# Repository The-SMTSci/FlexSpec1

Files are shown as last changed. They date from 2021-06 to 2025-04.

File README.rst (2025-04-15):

FlexSpec1
=========

 

Small telescope Flexible Spectrograph One.

Check out the documentation: 

`FlexSpec1 ReadTheDocs.io <https://flexspec1.readthedocs.io/en/latest/>`_

Serial Ports
------------

The later Rpi 4's are based on BCM2835 processor, and uses the
PL011 UARTs. 

.. list-table:: RPi 4 UART and Device Assignments
   :widths: 10 25 25 50 50
   :header-rows: 1

   * - UART
     - RX Pin (Board)
     - Tx Pin (Board)
     - Comm Port
     - Conflicts
   * - uart0 
     - GPIO 14    8  
     - GPIO 15   10  
     - /dev/ttyAMA0 
     - Serial Console
   * - uart1 
     - GPIO 0    27  
     - GPIO 1    28  
     - /dev/ttyAMA1 
     -
   * - uart2 
     - GPIO 4     7  
     - GPIO 5    29  
     - /dev/ttyAMA2 
     - I2C
   * - uart3 
     - GPIO 8    24  
     - GPIO 9    21  
     - /dev/ttyAMA3 
     -
   * - uart4 
     - GPIO 12   32  
     - GPIO 13   33  
     - /dev/ttyAMA4 
     - SPI0
   * - uart5
     - GPIO 12   14
     - GPIO 13   15
     - /dev/ttyAMA5

Other Interfaces
----------------

# Enabling I2C3, with SDA on GPIO4 and SCL on GPIO5
dtoverlay=i2c3,pins_4_5

History:
--------

V0.0 - pre-release placeholder.





PuTTY Commands:
+++++++++++++++

.. list-table:: PuYTTY FlexSpec1 Serial Port Commands
   :widths: 10 25 90
   :header-rows: 0

   * - A<CR>
     - 
     - All functions list
   * - B<CR>
     - 
     - Blue LED
   * - C<CR>
     - 
     - Configuration to set the grating lines per mm
   * - F<CR>
     - 
     - Focus the collimating lens
   * - G<CR>
     - 
     - Green LED lights the Green
   * - H<CR>
     - 
     - Home The Grating
   * - I<CR>
     - <PWM>
     - Incandescent Grain of Wheat Flat lamps, PWM 0 - 100%.
   * - J<CR>
     - 
     - Used to center zero order to focus on slit
   * - L<CR>
     - <PWM>
     - Flat Lamp lights the LED Flat lamps, PWM 0 - 100%.
   * - M<CR>
     - 
     - Reset collimating Focuses to zero
   * - N<CR>
     - 
     - Neon / Calibration
   * - O<CR>
     - 
     - Off Turns all lamps off
   * - Q<CR>
     - 
     - Query status of the spectrometer
   * - R<CR>
     - <PWM>
     - Red LED Controls The Red LED With PWM 0 - 100%
   * - S<CR>
     - 
     - Shutter  (Open Close Toggle)
   * - U<CR>
     - <PWM>
     - UV Boost Lights the UV Boost, PWM 0 - 100%.
   * - V<CR>
     - 
     - Viewer for Slit. Backlight View the slit with backlight
   * - W<CR>
     - <Integer>
     - Wavelength rotate the grating to center desired wavelength
   * - Z<CR>
     - 
     - Zero Collimating lens to position = 0 (home)
   * - 
     - 
     - (This should only be done once on initialization of
   * - 
     - 
     - physical focus)
   * - 
     - 
     - 
   * - ?<CR>
     - 
     - Query the Defines the grating and collimating motor direction
   * - 
     - 
     - (This should only be done once on initialization or
   * - 
     - 
     - if a motor is changed depending on the manufacture
   * - 
     - 
     - some motors run in oposit direction)

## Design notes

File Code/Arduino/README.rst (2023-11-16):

FlexSpec1 Arduino Directory
===========================

An Arduino program consists of a *.ino* file, that acts like the main program.

The Arduino IDE/Compilers require the .ino file to be in a directory with the
same name. For example:  demos/hello/hello.ini is inside a directory called hello.

Any other file in the directory that ends in *.c*, *.cpp*, *.h*" will also
be compiled and linked into the code. So if you have a file call extras.cpp
and you want to keep it around as a temporary backup call it extras.cpp.bak
and it will be ignored.

Arduino code ***IS*** "--std=c++11" and "-fno-exceptions". This means quite
a few interesting new code features are available, like auto, looping extensions
etc. However it also means that "try/throw/catch" exception mechanism is 
disabled. The exception mechanism uses quite a bit of code.

Avoid anything that refers to "iostream" This brings in quite a lot of code.

C is a proper subset of C++, so do not feel compelled to use lots of C++
features.

ARM Boards, BLE/IoT and Seeduino Xaio
-------------------------------------

Boards are made to be compilent with different vendors environments. One is Mbed
and the other is SAMD. In some cases, libraries are written to take advantage
of only one environment's features! Thus code that compiles on one will fail
on another.

In the main .ino file, please use the IDE to gather the version and author's
name for each library package used. This helps to avoid confusion later.

This Directory
--------------

1. Demos
   a. hello : Print the word hello to the serial ports.
   b. gigo: Characters that are read, are printed right back. Handy for testing the CR/LF and baud rates.
2. MainBoard
   a. FlexSpec
3. Kzin
   a. Kzin

Serial Communications
---------------------

The USB hardware in Arduinos, may not work well with the USB hardeare
found in hubs and main motherboards. This does cause some issues.

The clock rates of Arduinos are not that precise. 9600 baud may be 
a tad bit slower/faster -- but the protocol usually does not trip
over small differences.

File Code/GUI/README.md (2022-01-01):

GUI
===

The GUI has several subsystems:

# The "matching classes" py together with Arduino's C++
# The underlying algorithms as resources, now being developed under
# django in a container.

FlexSpec1/Code/GUI/

README.md
main

---
2021-12-31T11:36:29-0700

Zoom meeting: 3 papes:
1) collimator (maths etc)
2) guider (maths etc)
3) kzin ring (flats)
Perhaps a few newsletters...

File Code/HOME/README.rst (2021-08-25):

README
======

The HOME directory has some basic things to copy to home directories
for users of the Raspberry Pi.

pi.aliases - aliases, and alterations to terminals to make the system
  livable.

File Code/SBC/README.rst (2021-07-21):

Single Board Computer Code
==========================

This directory holds the code needed to support the Bokeh interface
to the rest of the world.

server.py -- The stub of a server. DEVELOPING

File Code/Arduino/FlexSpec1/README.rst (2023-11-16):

FlexSpec1
=========

The current version is 4.1.2, its md5sum is: db0fdba5357043d4d449a2c6e9d09390.

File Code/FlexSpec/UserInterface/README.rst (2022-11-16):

README
======

Testing can be done with Chrome in incognito mode (does't clutter
up cookies).

This approach uses a "matched class" and a "data driven" approach.
The 'def send_state(self) is the gateway to Flex dispatch server for
    each class.

FlexSpec.py - instantiate/layout the gadgets we're currently supporting:
   KzinBokeh.py
   Collimator.py
   GratingBokey.py GrratingDefinition.py
   ParallacticAngle.py
   Shutter.py  (Needs to be developed fully)

Other Gadgets:
      EEPROMBokeh.py
      BlinkyBokeh.h

Good to have:
     Site.py
     TargetsBokeh.py
     FITS/FITS.py       -- brew up header for the instrument

The objects to use/develop:

    BlinkyBokeh.py       - Test more than anything
    CameraFocusBokeh.py  - NOT the 'camera' lens
    Collimator.py        - drive the collimator motors
    EEPROMBokeh.py       - manage an eeprom filesystem     FlexEEPROM.py        -
    FITS.py              - FlexSpec FITS header details, fits format
    FlexSpec.py          - A class for the device itself
    GratingBokeh.py      - Motors and configuration of  a grating
    GratingDefinition.py - Definition of lots of gratings to choose
    Guider.py            - NOT focus/rotate the guider
    KzinBokeh.py         - Manage the cal lamps and the shutter
    LampBokeh.py         - ?
    Network.py           - GUI/Dispatch server management
    ParallacticAngle.py  - pangle - get/report the parallactic angle
    Shutter.py           - Deal with the shutter itself
    Site.py              - Site details
    SlitBokeh.py         - Select and manage slit details
    TargetsBokeh.py      - NOT state the curent target details

TBD: FITS.py, Site,Targets. Network

Not clearly defined.... FlexPublish.py       -

RunFlexSpec

Two classes -- A python class at the Bokeh level and a C++ class in the
Arduino have their data synchronized. The user's request is tested and all
error checking in performed at the Bokeh class then an image of the
variables' state is sent to the matched Arduino C++ partner class.
The C++ class strives to "match the request" and will achieve a final
state. For example a request for 5000 angstroms for a grating's central
wavelength may fall between 4995 and 5007 due to cogging of the control
motor. Assuming perfect backlash, the C++ class may choose 4995. It
then reports its state back to the Bokeh class -- the Bokeh updates
the user's interface to reflect the "current state-of-affairs" of the
remote device. The governing rule is the remote device takes precedence
over the display. The display strives to portray the remote state-of-affairs.

Release Note:
2022-08-09T08:20:31-0600

Several modules were sending actual non-quoted integer/float
values. This was corrected though there may be a few missed
cases. While the code was open, a few major internal changes
were implemented. This does not effect the general operation.

The main visible change is the 'Display' pane now outputs
text that may be cut then pasted into Python. This is more
for checking results by hand. This work is leading to
a log message.

The code was re-worked for formatting, nomenclature (Display was
changed to FlexPublish to reflect what it really does), the layout
variable names changed to reflect their actual order etc.  Comments
were added, formatting of the code, usual beautification things.

Work has began on the serial interface extension(s) to the
main backend dispatch server. Written in python, with the
target machine being the Raspberry Pi 4B+.

.. note::

    myapp
       |
       +---__init__.py
       +---app_hooks.py
       +---main.py
       +---request_handler.py
       +---static
       +---theme.yaml
       +---templates
            +---index.html

.. note::

    myapp
       |
       +---__init__.py
       |
       +---app_hooks.py
       +---data
       |    +---things.csv
       |
       +---helpers.py
       +---main.py
       |---models
       |    +---custom.js
       |
       +---request_handler.py
       +---static
       |    +---css
       |    |    +---special.css
       |    |
       |    +---images
       |    |    +---foo.png
       |    |    +---bar.png
       |    |
       |    +---js
       |        +---special.js
       |
       |---templates
       |    +---index.html
       |
       +---theme.yaml

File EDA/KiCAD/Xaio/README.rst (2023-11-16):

Xaio Standalone Board
=====================

Schematics
-----------

KiCAD Files
-----------

* XAIO-B1-A-cache.lib
* XAIO-B1-A-rescue.dcm
* XAIO-B1-A-rescue.lib
* Xiao-B1-cache.lib
* Xiao-B1.kicad_pcb
* Xiao-B1.pro
* Xiao-B1.sch
* Xiao-KM1-a-cache.lib
* Xiao-KM1-a-recover.pro
* Xiao-KM1-a.d356
* Xiao-KM1-a.kicad_pcb
* Xiao-KM1-a.pro
* sym-lib-table

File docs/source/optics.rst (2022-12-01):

Care of Optics
==============

When handling optics uses gloves, nitrile or pure clean untreated
cotton gloves. This will protect the optical elements and protect
you from harsh cleaning chemicals. Optics should be stored in an
airtight container to avoid reaction with pollutants. 

#.  **Never** use silcone based adhesives or silicone based lubricants any 
    where near optics. They outgas and condense on the optical surfaces.

#.  The optics should never be touched with your bare hands.  Always
    use clean powder free latex or nitrile gloves. Finger prints leave
    oils, acids and other volatiles on the surfaces which in the cases of
    gratings can not be removed. On lenses or mirrors they may etch the
    surface coatings.

#.  If after careful handling a finger print gets on the surface a
    micro fiber cloth may remove it if used gently.  DON’T try to wipe a
    grating it will scratch.

#.  Front surface mirrors are also fragile. Usually they are over
    coated for protection but the coating may be very thin.

#.  Don’t use **Windex** |reg| to clean optics. It contains ammonia which
    can remove aluminum coating. Use Everclear |reg| grain alcohol, 95%
    ethanol alcohol or commercial lens cleaning solution as a cleaning
    fluid. Us it sparingly. Grain alcohol does not contain denaturing
    agents and should not leave a fine white powder on optics.

    Like most alcohols, isopropyl alcohol reacts with active metals
    such as potassium to form alkoxides that can be called
    isopropoxides. The reaction with aluminum (initiated by a trace
    of mercury) is used to prepare the catalyst aluminum
    isopropoxides. Most IPA isopropyl alcohol has denaturing
    agents added and will leave a fine white powder.

#.  Gratings are very susceptible to handling problems. Even with
    gloves never touch the ruled surface.  Any scratches or finger prints
    will introduce scattered light in to the system. A spectrograph is
    always starved for light and to scatter some of the light will reduce
    the throughput.

Tips for optics in a spectrograph
---------------------------------

#.  Grating orientation: if a commercial blazed grating is used it
    will have an arrow drawn on the top, bottom or both edges that are
    perpendicular to the grooves.  This arrow shows the blaze
    direction. The arrow should point toward the incoming beam.  This
    orientation maximizes the energy into the first order. If the
    arrow is missing it is possible to look into the spectrographs
    camera port, without the camera lens in place, while light is
    shinning on the slit, rotate the grating so that the zero’th order
    can be seen. Then rotate the grating further to pick up the
    spectrum starting with the blue end. Further grating rotation will
    the bring up the second order. The first order should be very much
    brighter than the second order.  If it isn’t the grating
    orientation in the holder should be reversed.

#.  If the dispersion along the image from the sensor is not
    horizontal (follows a 'row' of pixels), the camera needs to be
    rotated such that it is. 

#.  If the calibration lamp emission lines are not vertical with
    respect to the grating; the OVIO slit needs to be rotated in it’s
    holder to make them vertical. This can be fiddly sometimes to get
    right. Also the vertical slit must be co-linear with the grating
    grooves.

#.  If lenses are not a snug fit into their holders a small
    application of white glue on the holder will hold them in place
    but allow later removal if needed. Don’t get a glue string on the
    lens.

#.  If the lens is a snug fit into the holder make sure that you don’t
    apply too much pressure to insert it. Some lower quality achromat
    lens elements are not glued in a way that is precisely centered
    and while pushing it in an edge might get caught and split the
    elements apart.

#.  Depending on many factors (lens focal length, aperture, quality)
    the blue and red ends of the spectra may be out of focus while the
    center is sharp. This is normal with simple achromat lenses used
    for the camera lens. If a commercial photographic lens is used for
    the camera lens this is much less of a problem as the multiple
    elements in the commercial lens are designed to flatten the field.

#.  When combined with large chips, short focal length lenses, with
    short radii may require the sensors plane to be shifted. This is
    easily achieved with after-marked sensor/camera tilt correctors.

#.  A Cheshire eyepiece (laser collimator) is a very handy tool to get
    things lined up in the spectrograph, particularly the guide mirror
    and main mirror. It is also an easy way to check if the grating is
    mounted with it’s surface parallel with the rotation stage. If it
    is a green laser and the grating stage rotated till the beam is
    centered in the camera port, then the first spectra will be close
    to centered. If red then adjust the grating angle such that it is
    where H-alpha emission is expected on the image.

#.  Achromat lens orientation. When mounting lenses the side with the
    bigger “bulge” should be oriented toward the grating. Both for the
    collimating lens as well as the camera lens.

.. |reg|    unicode:: U+000AE .. REGISTERED SIGN
.. |copy|   unicode:: U+000A9 .. COPYRIGHT SIGN

Adhesives
---------

ASTM E595 is the specification for low outgassing. 

Outgassing Data for Selecting Spacecraft Materials Online

https://outgassing.nasa.gov/

PDF about gasses of common filiments:
https://www.mdpi.com/1420-3049/27/12/3814/pdf?version=1655194705

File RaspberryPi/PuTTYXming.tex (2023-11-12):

% PuTTYXming.tex

\section*{PuTTY and Xming on Windows} \label{sec:puttyxming}
\setcounter{section}{1}

PuTTY running remotely on a Raspberry Pi uses X11 to share its
interface with the remote user. This may require XMing for Win11, and
XQuartz for Apple machines. It may require including a X11 desktop (in
lieu of Wayland) on the remote Linux machines.

This article addresses executing PuTTY on a Raspberry Pi from a Win1X
machine located elsewhere on the Internet. It addresses basic tactical
aspects of network configuration. Direct X11 and port-to-port TCP
methods sidestep the bandwidth overhead of VNC like environments.  The
office desktop is presumed to be a Win1X office desktop, but may be a
Linux desktop with built-in native X11 protocols\footnote{In X11, the
  XClient is the program with all the builtin domain/control logic --
  like a spreadsheet, that offers up a GUI connection. An XServer,
  with all the logic for window creation, managing user interaction
  and 'serving' back graphics etc ties the user to the XClient's
  logic. The XServer may be elsewhere on the network from the running
  program. The protocol is very light-weight compared to
  remote-desktop (VNC) methods.}\footnote{Note: The Wayland
  X11-Replacement may introduce X11 issues.}, or an Apple machine with
a proper X11 Server support package like XQuartz.  Linux is addressed
in section \ref{sec:PuttyLinuxDesktop}.

Win1X requires an X11 Server support program. Here the
Xming\footnote{Get Xming: https://sourceforge.net/projects/xming/} package is the
only one discussed.

The typographic conventions used in these notes.

Here \llbox{k} means hit the ``k'' on the keyboard. 

For the Win1X office desktop, it is important that you acquire and install:
\vspace{-.15cm}
\begin{enumerate}\addtolength{\itemsep}{-0.5\baselineskip}
%\setcounter{enumi}{N}
   \item   Win1X office desktop
\vspace{-.15cm}
\begin{enumerate}\addtolength{\itemsep}{-0.5\baselineskip}
%\setcounter{enumi}{N}
   \item   XMing
   \item   PuTTY
\end{enumerate}
   \item   Raspberry Pi
\vspace{-.15cm}
\begin{enumerate}\addtolength{\itemsep}{-0.5\baselineskip}
%\setcounter{enumi}{N}
   \item   PuTTY
\end{enumerate}
   \item   Optional Linux office desktop
\vspace{-.15cm}
\begin{enumerate}\addtolength{\itemsep}{-0.5\baselineskip}
%\setcounter{enumi}{N}
   \item   PuTTY
\end{enumerate}
\end{enumerate}

You need to configure XMing's XLaunch program. You need to configure the
Raspberry Pi's configuration.

The PuTTY program provides a X11/ssh connection to remote machines. Here
the machine's hostname is \dhl{stellarmate.local}, the port is 22.

Xming is a X11 ``server'' (meaning is backwards from a data center's
client/server sense). X11 ``serves'' the graphics from a remote machine
doing all the heavy computing on a light-weight machine that knows nothing
about the remote application.

Grab Xming and install on a Win machine.

First some X11 magic:

You will open a \dhl{ssh -X} connection to the Raspberry Pi. This
allows linux to display a console window on the Win1X office desktop
monitor. In that window (remember will start programs on the Raspberry
Pi) you will start a PuTTY program running on the Raspberry Pi that
causes its window to appear on the Win1X office desktop.

\begin{figure}[h!]
\centering

\caption[Win1X use.]{Win1X office desktop monitor uses TCP/IP and SSH
  with the -X switch to open a connection to Raspberry Pi. A PuTTY
  instance is started on the Raspberry Pi, configured for the USB port
  for the Arduino displays the PuTTY window on the remote desktop vi
  SSH -X working with Xming} %% \caption{{\tiny{citation}}}
\label{figure:Diagram1}
\end{figure}

\begingroup \fontsize{10pt}{10pt}
\selectfont
%%\begin{Verbatim} [commandchars=\\\{\}]
\begin{verbatim} 

Check the files in the /etc/X11 directory:
   /etc/X11/xinit/xserverrc
   ~/.xinitrc
   ~/.xsession  -- start programs when the login is complete
   ~/.profile

ssh-keygen -t ed25519 -C "your_email@example.com"

\end{verbatim}
\endgroup
%% \end{Verbatim}

If there is no /etc/X11

\verb=xmodmap -pke > ~/.Xmodmap # make a .Xmodmap upon which to hack=

This varies with new modern keyboards, there is massive
confusion over what a key is called and what code corresponds to
the key among keyboard vendors. 

To use the \dhl{caps lock} key as a spare \dhl{control} key find the
code for the caps lock key using the \dhl{xev} program. Xev will show
keycodes when a key changes state, like shift down, then shift up
etc...  

Hit the the ``caps'' key and note its code. Then edit the \dhl{~/.Xmodmap}
file and change:

\verb/keycode  37 = Control_L NoSymbol Control_L/

\newpage
\subsection{Remote Desktop PuTTY}

On the remote desktop, configure the remote PuTTY:

\vspace{-.15cm}
\begin{enumerate}\addtolength{\itemsep}{-0.5\baselineskip}
%\setcounter{enumi}{N}
   \item   Session:
\vspace{-.15cm}
\begin{enumerate}\addtolength{\itemsep}{-0.5\baselineskip}
%\setcounter{enumi}{N}
   \item   Select the \dhl{Serial} radio button
   \item   Serial Line to \dhl{/dev/ttyACM0}
   \item   Speed \dhl{9600}
   %\item   CTM\_X
   \item   Close window on exit $\rightarrow$ \dhl{Only on clean exit}
\end{enumerate}
   \item   Terminal
\vspace{-.15cm}
\begin{enumerate}\addtolength{\itemsep}{-0.5\baselineskip}
%\setcounter{enumi}{N}
   \item   In the \dhl{Line disipline options}:
\vspace{-.15cm}
\begin{enumerate}\addtolength{\itemsep}{-0.5\baselineskip}
%\setcounter{enumi}{N}
   \item  Local echo to \dhl{Force on}
   \item  Local line editing to \dhl{Force on}
\end{enumerate}
\end{enumerate}
   \item   Window
\vspace{-.15cm}
\begin{enumerate}\addtolength{\itemsep}{-0.5\baselineskip}
%\setcounter{enumi}{N}
   \item   Columns: \dhl{120} Rows: \dhl{50}
   \item   scrollback 200
   \item   display scrollbar
   %\item   Reset scrollback on display activity
   %\item   push erased text into scrollback
\end{enumerate}
   \item   Connection $\rightarrow$ Data
\vspace{-.15cm}
\begin{enumerate}\addtolength{\itemsep}{-0.5\baselineskip}
%\setcounter{enumi}{N}
   \item   login name can be set to \dhl{stellarmate} for stellarmate, or
     the remote user's name.
   \item   Terminal-type string xterm
   \item   Terminal Speed 38400, 38400
\end{enumerate}
\item SSH
\vspace{-.15cm}
\begin{enumerate}\addtolength{\itemsep}{-0.5\baselineskip}
%\setcounter{enumi}{N}
   \item   Remote Command to \dhl{/home/stellarmate/bin/flex.py}
\end{enumerate}

   \item   SSH$\rightarrow$X11

\vspace{-.15cm}
\begin{enumerate}\addtolength{\itemsep}{-0.5\baselineskip}
%\setcounter{enumi}{N}
   \item   Enable X11 forwarding
   \item   localhost:0.0
   \item   MIT-Magic-Cookie-1
\end{enumerate}
\vspace{-.15cm}
\begin{enumerate}\addtolength{\itemsep}{-0.5\baselineskip}
%\setcounter{enumi}{N}
   \item   Serial
\vspace{-.15cm}
\begin{enumerate}\addtolength{\itemsep}{-0.5\baselineskip}
%\setcounter{enumi}{N}
   \item   Baud to 9600
   \item   Data bits 8
   \item   Stop bits 1
   \item   Parity None
   \item   Flow Control None.
\end{enumerate}
\end{enumerate}

\end{enumerate}

\begin{figure}[h!]
\centering

\caption{PuTTY screen snaps of the 4 configuration menu panels.} %% \caption{{\tiny{citation}}} 
\label{figure:PuYYTXming}
\end{figure}

\newpage
\subsection{Remote Desktop Xming}

On the Windows pane, enter a new configuration for this machine.

\vspace{-.15cm}
\begin{enumerate}\addtolength{\itemsep}{-0.5\baselineskip}
%\setcounter{enumi}{N}
   \item Page 1 - Set Multiple windows (Each remote application gets
     its own Win1X office desktop window).
   \item Page 2 - Start no client. The clients are started with the
     Win1X PuTTY's SSH -X session.
   \item  Page 3 - Clipboard (handy)
   \item Page 4 - Save the configuration. This sets the policy for all
     machines, Xming does not care about the remote machines business
     -- any remote may connect if firewall permissions are set.
\end{enumerate}

\begin{figure}[h!]
\centering

\caption{Xming screen snaps of the 4 configuration menu panels.} %% \caption{{\tiny{citation}}} 
\label{figure:XmingConfig}
\end{figure}

\input{Raspberry.tex
}

\subsection{StellarMate} \label{sec:StellarMate}

You need to \dhl{sudo apt update}, then \dhl{sudo apt install putty -y}
to install PuTTY.

Add the \dhl{x11-utils} package to pick up the rather silly command
xeys. This displays two white eyeballs and the pupils track the mouse
movement. While small and cute, it does a rather deep test of the X11
capability including managing the event manager. This is helpful
to debug X11 connnections.

\begin{quote}
\dhl{sudo apt install -y x11-utils}
\end{quote}

Other programs:
\begin{quote}
\dhl{sudo apt install -y saoimage-ds9}  \\
\dhl{sudo apt install -y iraf}          \\ 
\dhl{sudo apt install -y python3-pyraf}
\end{quote}

The ssh connect to StellarMate is made to an alternate port:

\dhl{ssh -X -p 5624 stellarmate@stellarmate.local}

The username is \dhl{stellarmate} and the password is the usual
StellarMate password.

\section{Using Putty from Linux Desktop} \label{sec:PuttyLinuxDesktop}

PuTTY on a linux desktop machine in the office has all the Xming features
built-in and does not require additional X-windows code.

\section{Linux Ports}

devices such as serial ports, USB ports etc appear simply as
filenames.  For example the Arduino often identifies as
\dhl{/dev/ttyACM0}. By making no distinction using devices becomes
very easy but drives Win1X people nuts.

See section \ref{sec:RPiSerialPorts} for details about the Raspberry Pi.

The ports you are interested in:

\vspace{-.15cm}
\begin{enumerate}\addtolength{\itemsep}{-0.5\baselineskip}
%\setcounter{enumi}{N}
   \item   /dev/serial0 - the serial port pins on the Raspberry Pi. This requires 
special action to enable the GPIO pins. This is recognized by the Arduino on its Serial1
 device.
   \item   /dev/ttyAMC0 - the USB port recognized by the Arduino on its Serial
 device.
\end{enumerate}

\section{Running the Arduino CLI on the Raspberry Pi}

The Raspberry Pi will run the Arduino CLI, which in turn may run a
serial port connection. Using the magic of X11, discussed above, the
Arduino CLI windows will appear on the Win1X office desktop monitor or
Linux office desktop monitor.

From the Win1X machine:

\vspace{-.15cm}
\begin{enumerate}\addtolength{\itemsep}{-0.5\baselineskip}
%\setcounter{enumi}{N}
   \item   Use Xlaunch with multiple windows.
   \item   Then make a PuTTY connection to the RPi. (Call this Win1X/Rpi)
\vspace{-.15cm}
\begin{enumerate}\addtolength{\itemsep}{-0.5\baselineskip}
%\setcounter{enumi}{N}
   \item   this opens a Win1X cmd window, and prompts for the password into
 the RPi machine.
   \item   A Rpi prompt will appear.
\end{enumerate}

   \item   In the Win1X/Rpi window (now a shell on the RPi)
\vspace{-.15cm}
\begin{enumerate}\addtolength{\itemsep}{-0.5\baselineskip}
%\setcounter{enumi}{N}
   \item   enter the command \dhl{putty {-}{-}display=\$DISPLAY} (two dashes)
   \item   This causes a PuTTY configuration window from the RPi to appear on the 
           Win1X desktop.
   \item   Configure for the serial connection desired \dhl{/dev/ttyAM0} for
          the Arduino.
\end{enumerate}

\vspace{-.15cm}
\begin{enumerate}\addtolength{\itemsep}{-0.5\baselineskip}
%\setcounter{enumi}{N}
   \item   Run
   \item   This causes a PuTTY serial console (as you configured it) to appear on the
 Win1X desktop.
   \item   Interact with the Arduino, at the end of a UART serial connection, with
   the FlexSpec1 instrument -- as though you were at the Rpi.
\end{enumerate}
\end{enumerate}

You may wish to install \dhl{xeyes} program on the RPi. Xeyes 
is a rather simplistic X11 program that causes a little window
to pop-up with two ``eyeballs'' where the ``eyes'' will watch the
mouse move around. This tests mouse and graphics in on go. To
do so -- in the Win1X/Rpi console enter: 

\begingroup \fontsize{10pt}{10pt}
\selectfont
%%\begin{Verbatim} [commandchars=\\\{\}]
{\color{verbcolor}
\begin{verbatim} 
sudo apt install x11-utils
\end{verbatim}
}
\endgroup
%% \end{Verbatim}

\subsection{Additional Resources}

\url{http://www.straightrunning.com/xmingnotes/IDH_PROGRAM.htm}

\subsection{More than One Win1X connection}

Make Desktop Icon's for unique connections:

\vspace{-.15cm}
\begin{enumerate}\addtolength{\itemsep}{-0.5\baselineskip}
%\setcounter{enumi}{N}
   \item  Run XLaunch.exe and save the configuration to file config.xlaunch.
   \item  Create a shortcut of XLaunch.exe under Startup directory.
   \item Modify the target field of the shortcut to
     \verb="C:\ZZH\software\Xming\XLaunch.exe" -run "config.xlaunch"=.
\end{enumerate}

\subsubsection{Another approach to autostart with Win1X}
\vspace{-.15cm}
\begin{enumerate}\addtolength{\itemsep}{-0.5\baselineskip}
%\setcounter{enumi}{N}
   \item  Search for Xming in the Start Menu
   \item  Right click on the shortcut and select Open file location
   \item  Copy the selected Xming shortcut
   \item  Press Ctrl-l to move the cursor to the Explorer location input
   \item  type shell:startup and then Enter
   \item  Paste the Xming shortcut in the Startup directory.
\end{enumerate}

\section{Auditing}

It is possible to save the and/or share the configuration parameters
for PuTTY.

\subsection{Windows}

PuTTY on Win1X records its configuration(s) into the Registry. It
requires the dangerous step of using Regedit to recover. The steps are:

\vspace{-.15cm}
\begin{enumerate}\addtolength{\itemsep}{-0.5\baselineskip}
%\setcounter{enumi}{N}
   \item   Find  \verb=HKEY_CURRENT_USER\Software\SimonTatham\PuTTY=
  Note: The ``SimonTatham'' is the name of the author of the package
  not you, the ``CURRENT\_USER''.
   \item   Right click and export, the resulting file is a text file suitable
  for sharing and archiving.
\end{enumerate}

\subsection{Linux}

The configuration file is in \dhl{\$HOME/.putty} deep.

% hostname to stellarmate  port 5624

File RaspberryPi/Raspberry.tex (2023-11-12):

Details for the Raspberry Pi.

\newpage
\section{Raspberry Pi}

Details related to the Raspberry Pi.

\subsection{SSH on Raspberry Pi}

The StellarMate image has all necessary ports open and ready for use.
The firewall has been set to pass all relevant ports.

See subsection \ref{sec:StellarMate} below.

\subsection{Non-StellarMate Raspberry Pi's}

Note: this section is complicated by the details needed to open
home firewalls to the internet using the local Telco's interface
routers. Each router is different, and the Telco changes its mind
frequently.

This command will list the full name for hosts that are on the network.
Here we're looking for our machine \dhl{pier15} that will appear
as \dhl{pier15.hsd1.co.comcast.net}:

{\color{verbcolor}{\verb={sudo nmap -sP 10.1.10.0/24 | awk -e '/^Nmap/ {print $5;}'}=}}

If ssh issues a:

\dhl{ssh: connect to host <machine>.local port 22: Connection refused}

use the keyboard/mouse for the raspbian machine and run the command
\dhl{sudo raspi-config}, then under Interface options, \dhl{I2 SSH} \llbox{{TAB}}, enable.

SSH (Secure SHell), originates on port 22. The port needs to be allowed
through the Raspbian's ``uncomplicated firewall'' \dhl{ufw} task. Root
permissions are required.

\begingroup \fontsize{10pt}{10pt}
\selectfont
%%\begin{Verbatim} [commandchars=\\\{\}]
\begin{verbatim} 
sudo ufw list       # see all the current ports
sudo ufw allow ssh  # allow the port to work.
\end{verbatim}
\endgroup
%% \end{Verbatim}

\subsection{Raspberry Pi -- Raspbian SSH}

Enable SSH through the Raspberry Pi Configuration menu:
\dhl{Preferences $\rightarrow$ Raspberry Pi Configuration} Click on ``Interfaces'':
and select \dhl{Enabled} next to SSH.

Use the command \dhl{sudo nano /etc/ssh/sshd\_config} find
and X11Forwarding set the value to yes 

\dhl{ X11Forwarding yes}.

Save.

\dhl{sudo systemctl restart ssh}

% https://techsphinx.com/raspberry-Pi/enable-x11-forwarding-on-raspberry-Pi/

\subsection{Serial Ports}

At end of file:

\begingroup \fontsize{10pt}{10pt}
\selectfont
%%\begin{Verbatim} [commandchars=\\\{\}]
\begin{verbatim} 
dtoverlay=disable-bt
dtoverlay=uart1
dtoverlay=uart2
droverlay=uart3
dtoverlay=uart4
dtoverlay=uart5
\end{verbatim}
\endgroup
%% \end{Verbatim}

Pinouts:

\begingroup \fontsize{10pt}{10pt}
\selectfont
%%\begin{Verbatim} [commandchars=\\\{\}]
\begin{verbatim} 
0/1    14/15   Same Uart
2       0/1
3       4/5
4       8/9
5      12/13
\end{verbatim}
\endgroup
%% \end{Verbatim}

To disable the Bluetooth 

\dhl{sudo systemctl disable hciuart}

\dhl{/boot/cmdline.txt:}

add \dhl{console=ttyS0,115200} to the main line.

\newpage
\subsection{Raspberry External Pin Functions}

\begingroup \fontsize{10pt}{10pt}
\selectfont
%%\begin{Verbatim} [commandchars=\\\{\}]
\begin{verbatim} 
  ALT0       ALT1       ALT2       ALT3       ALT4       ALT5      
 0 SDA0       SA5        PCLK       SPI3_CE0_N TXD2       SDA6      
 1 SCL0       SA4        DE         SPI3_MISO  RXD2       SCL6      
 2 SDA1       SA3        LCD_VSYNC  SPI3_MOSI  CTS2       SDA3      
 3 SCL1       SA2        LCD_HSYNC  SPI3_SCLK  RTS2       SCL3      
 4 GPCLK0     SA1        DPI_D0     SPI4_CE0_N TXD3       SDA3      
 5 GPCLK1     SAO        DPI_D1     SPI4_MISO  RXD3       SCL3      
 6 GPCLK2     SOE_N      DPI_D2     SPI4_MOSI  CTS3       SDA4      
 7 SPI0_CE1_N SWE_N      DPI_D3     SPI4_SCLK  RTS3       SCL4      
 8 SPI0_CE0_N SDO        DPI_D4     _          TXD4       SDA4      
 9 SPI0_MISO  SD1        DPI_D5     _          RXD4       SCL4      
10 SPI0_MOSI  SD2        DPI_D6     _          CTS4       SDA5      
11 SPI0_SCLK  SD3        DPI_D7     _          RTS4       SCL5      
12 PWM0       SD4        DPI_D8     SPI5_CE0_N TXD5       SDA5      
13 PWM1       SD5        DPI_D9     SPI5_MISO  RXD5       SCL5      
14 TXD0       SD6        DPI_D10    SPI5_MOSI  CTS5       TXD1      
15 RXD0       SD7        DPI_D11    SPI5_SCLK  RTS5       RXD1      
16 FL0        SD8        DPI_D12    CTS0       SPI1_CE2_N CTS1      
17 FL1        SD9        DPI_D13    RTS0       SPI1_CE1_N RTS1      
18 PCM_CLK    SD10       DPI_D14    SPI6_CE0_N SPI1_CE0_N PWM0      
19 PCM_FS     SD11       DPI_D15    SPI6_MISO  SPI1_MISO  PWM1      
20 PCM_DIN    SD12       DPI_D16    SPI6_MOSI  SPIl_MOSI  GPCLK0    
21 PCM_DOUT   SD13       DPI_D17    SPI6_SCLK  SPI1_SCLK  GPCLK1    
22 SD0_CLK    SD14       DPI_D18    SD1_CLK    ARM_TRST   SDA6      
23 SD0_XMD    SD15       DPI_D19    SD1_CMD    ARM_RTCK   SCL6      
24 SD0_DATO   SD16       DPI_D20    SD1_DAT0   ARM_TDO    SPI3_CE1_N
25 SD0_DAT1   SD17       DPI_D21    SD1_DAT1   ARM_TCK    SPI4_CE1_N
26 SD0_DAT2   TE0        DPI_D22    SD1_DAT2   ARM_TDI    SPI5_CE1_N
27 SD0_DAT3   TE1        DPI_D23    SD1_DAT3   ARM_TMS    SPI6_CE1_N
\end{verbatim}
\endgroup
%% \end{Verbatim}

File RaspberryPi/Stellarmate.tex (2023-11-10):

\section{Stellarmate}

\subsection{Paramount}
This page helps with installation for Paramount:
https://www.indilib.org/devices/mounts/bisque-paramount.html

\begin{figure}[h!]
\centering
\begingroup \fontsize{10pt}{10pt}
\selectfont
\begin{verbatim} 
# if using a Paramount
apt-add-repository ppa:mutlaqja/ppa
apt-get update 
sudo apt-get install libindi

cat >> /home/stellarmate/help.txt <<EOF
Paramount: In TheSkyX preferences, make sure to turn off TCP Responses close socket.
EOF
\end{verbatim}
\endgroup
\caption{Raspberry Pi, Paramount packages to install.}
\label{figure:RaspberryPiParamount}
\end{figure}

Stellarmate uses the TCP connection for the mount. Needs port address of the mount's
PC.

From \url{https://www.indilib.org/devices/mounts/bisque-paramount.html}

\begin{figure}[h!]
\centering

\caption[TheSkyX preferences]{In TheSkyX preferences, make sure to turn off TCP Responses close socket}
\label{figure:SmateTheskyxConfig}
\end{figure}

\begin{figure}[h!]
\centering

\caption[Stellarmate paramount options]{Fill in the telescope parameters, and set
up to record to a log file.}
\label{figure:SmateParamountOptions }
\end{figure}

\begin{figure}[h!]
\centering

\caption[Stellarmate paramount connection]{Stellarmate paramount connection, this is
the IP address of the Sky X Computer, default port (3040) for TCP control.}
\label{figure:SmateParamountConnection.png}
es
\end{figure}

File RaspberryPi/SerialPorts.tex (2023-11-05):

\section{RPi Serial Ports} \label{sec:RPiSerialPorts}

The Raspberry Pi has 6 serial ports, available in various ways, including
over BlueTooth connections. The ports use GPIO pins, and may be disabled
to allow secondary functions for the GPIO pins to be permitted.

\begin{table}[h!]
\centering
\begin{tabular}{| l | l | l | l | l | l | l |}
%\MakeShortVerb{\|}
%\multicolumn{n}{fmt}{text for merged cols}
\hline
Name   &  Type       &  Models     &  Enabled    &  GPIO (TX)  &  GPIO (RX)  &  CTS/RTS    \\
\hline
UART0  &  PL011      &  All        &  Yes        &  14,32,36   &  15,33,37   &      \\
UART1  &  mini-UART  &  All        &  No         &  14,32,40   &  15,33,41   &      \\
UART2  &  PL011      &  Pi4 Only   &  No         &         0   &         3   &   2,3    \\
UART3  &  PL011      &  Pi4 Only   &  No         &         4   &         7   &   6,7    \\
UART4  &  PL011      &  Pi4 Only   &  No         &         8   &        11   &   10,11    \\
UART5  &  PL011      &  Pi4 Only   &  No         &        12   &        15   &   14,15    \\
%% ones-based: \cline{a-b}
\hline
%%\DeleteShortVerb{|}
\end{tabular}
%%\end{minipage}    %% for footnotes  r@{.}l
\caption[WAN Firewall]{Stellarmate WAN Firewall Ports}
\label{table:StellarmateWANFirewallPorts}
%%} % end small etc
\end{table}

\subsection{Connecting FlexSpec1 via Serial Ports}

The Serial Ports for the RPi are 3.3V and require a level shifter to be
on the safeside. The FlexSpec1 design calls for a 5-wire cable between
the RPi and the Arduino SBC. These include:

\begin{table}[h!]
\centering
\begin{tabular}{| l | l |}
\hline
RPi      &  RPi                         \\
+5 V     &  Power                       \\ 
GND      &  Signal/Electrical Ground    \\ 
Tx       &  Commands                    \\ 
Rx       &  Response                    \\ 
Reset    &  Reboot FlexSpec1            \\ 
%% ones-based: \cline{a-b}
\hline
\end{tabular}
\caption[RPi/Ardiuno Cable]{The Cable has a footprint on the FlexSpec
PCBA. Pins are shown for programming clarity. The pins on the Arduino
are lables and NOT traditional pin numbers. Be careful.}
\label{table:RPi/ArdiunoCable}
\end{table}

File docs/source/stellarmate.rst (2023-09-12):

Stellarmate on RPi
==================

The Flexspec leverages a Raspberry Pi 4B 4GB memory for its operation.
We do not recommend VNC connections as they are un-necessary and take
a lot of bandwidth to support -- particularly in shared remote observatory
settings. The RPi's Raspbian/Debian operating system fully supports X11.
Win1x boxes may run the Xming program as a XServer (client and server
terms are reversed in X11). 

Service           Port           WAN/Internet Control
SSH               5624           Required for Flexspec
INDI Web Manager  8624           Not required
INDI Server       7624           Not required
EkosLive Server   3000           Not required

Web VNC           6080           Not required
VNC               5900           Not required

Serial            /dev/ttyn      Arduino Serial1 pins on RPi
Serial            /dev/ttyADM0   Arduino Serial USB

The FlexSpec uses a 5 wire bundle to supply power, ground, 
RX, TX and a hard reset signal to the Arduino. The software
looks for commands on Serial1 and may supplies optional 
status information on the USB Serial interface. This requirements
off-loads traffic from and frees for use one USB port.

Of the USB Ports:

   # Science camera
   # Guide Camera
   # Optional wide field "finder camera", otherwise not required.
   # Optional Serial1 interface, otherwise not required.

Feathering the Nest
-------------------

The following packages may be loaded:
sudo apt-get install x11-utils            # xeyes for testing X
sudo apt install iraf                     # focus, analysis
sudo apt install pyraf3
sudo apt install locate                   # fast find of files.

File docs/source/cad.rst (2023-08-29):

CAD Computer Aided Design
=========================

The main design cycle consists of experiments, hand sketches, capture
of the sketches into one of the main CAD packages, to produce STL
files. STL files :index:`STL files` are converted into ``gcode`` using a slicer like Cura :index:`Cura`, moved to
the printer using ``Octoprint`` :index:`Octoprint` and printed. The 3D parts are
evaluated and (altered within this cycle) as needed.

Parts are easily shared across the world, via email or the GitHub we maintained while developing the spectrograph.

Flex Spec 1 relied heavily on CAD programs:

#. SolidWorks Known to a few of the Authors from previous lives. We are currently using the Solidworks 3DConnection (maker edition)

#. Autodesk's Fusion/360 popular (indeed basis for LowSpec). Autodesk is not as freely accessible to the community as before.

#. TinkerCAD modify STL files, capture basic designs.

#. FreeCAD, a pythonic 3D parametric modeler that is well supported by its community.

#. Cura convert STL into gcode

#. KiCAD for the electrical layout. The Power Supply Board was used.

#. Octoprint, used to readily transfer gcode to the 3D printer.

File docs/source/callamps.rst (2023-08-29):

Calibration Lamps
******************

Take reference calibration images, and maintain an archive and a PDF
of graphs of results. You may note changes, and account for
variations that will occur overtime.

Kzin :index:`Kzin` ring [Niven-Ellis]_ is the name assigned to our "ring-like"
in-line passive dispersing element equally illuminated by NeAr lamps,
LEDs, and small incandescent grain-of-wheat bulbs. The ring is shaped
in a way to reside inside the 2-inch nose-piece area outside of the
main housing of Flex Spec 1 (and other spectrographs) as not to take up valuable back-focus area
for popular SCTs. The permanent position of the Kzin ring means
repeatability in injecting the calibration source-light into the
spectrograph.

It has its own Arduino :index:`Kzin;Arduino`, and is controlled by a
series of software switches tied to the main functions. The new 2023 board now
uses Pulse Width Modulation (PWM) to adjust each lamp's (except the NeAr lamp) output level.

.. _BlueGreen1:
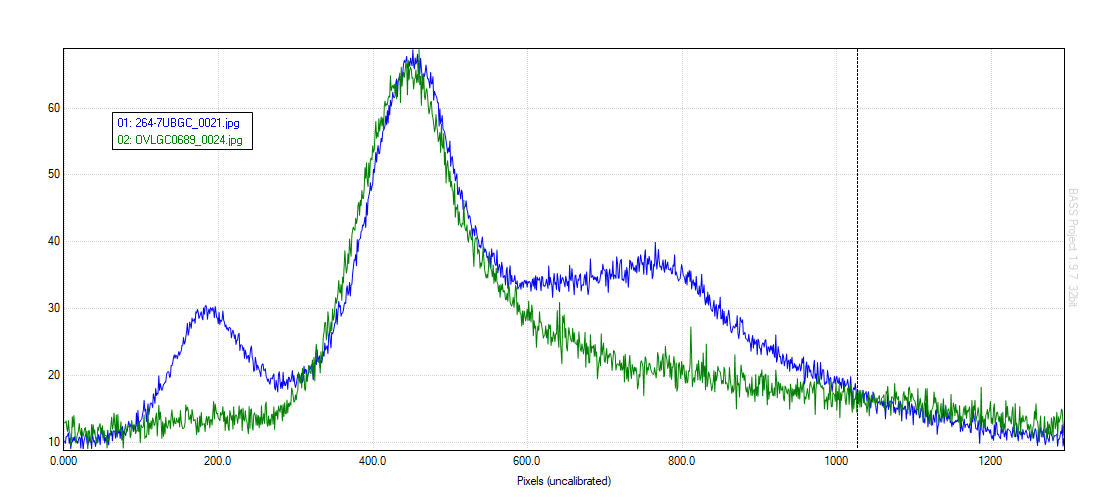
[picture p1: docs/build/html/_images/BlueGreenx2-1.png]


   Two LEDs listed as Blue-Green.

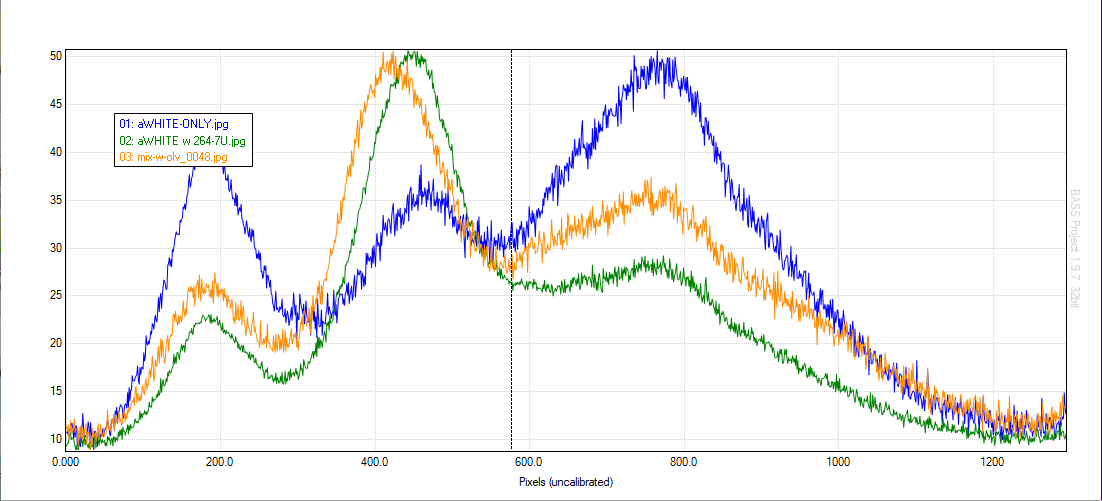
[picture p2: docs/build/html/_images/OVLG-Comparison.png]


   OVLG Leds marked as white.



   White Flashlight.

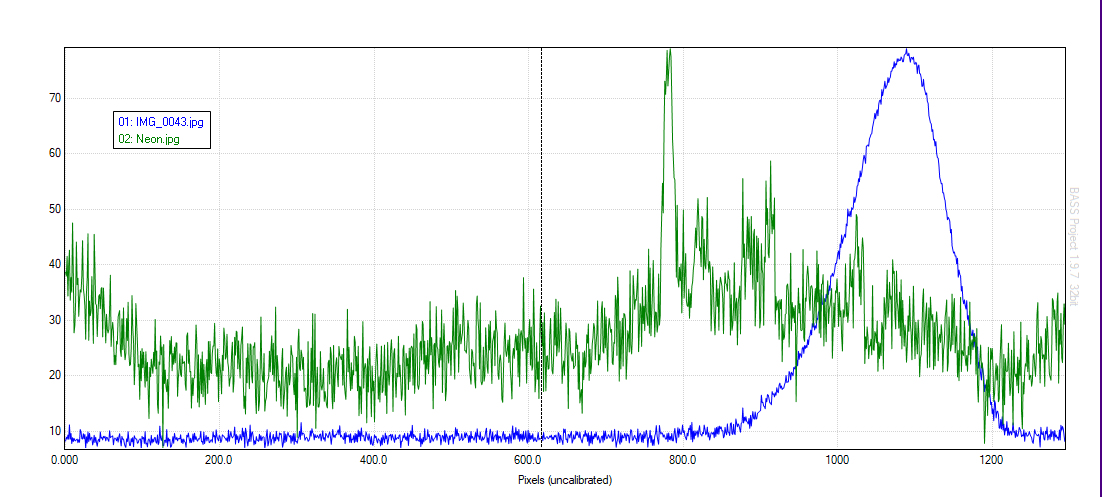
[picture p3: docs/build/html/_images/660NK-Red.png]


   660nm Red LED As 'finder' marker for grating central wavelength selection.

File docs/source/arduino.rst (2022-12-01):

Arduino Chips
=============

The Arduino project introduces people to both hardware and software design.
This package hides a massive amount of detail, and bends some of the basic
C/C++ approaches to program execution. Here are a few details you need to
know.

#. The main program (project) is called a 'sketch' and has a **.ino** extension.

#. A program called **foo** with its **foo.ino** file must reside in a directory called **foo** (with out the .ino extension). 

#. Any other **.h** or **.cpp** file that is in the foo directory will be automatically scanned, compiled and linked to form the main program. This is what FS1 does.

#. External packages are processor-dependent. They are managed by the "Preferences" and the "Tools/Manage Library" sub-menus. 

#. Some packages have the same name and may the IDE may confuse itself.

#. GCC error messages are pretty cryptic -- but with practice you sorta get used to them. 

Arduino does not use a 'sketch' language -- it uses **C++11** without
exception handling. The C++ features **try/throw/catch** are disabled and 
cause issues. 

Arduino uses a lot of hidden build tricks that are unfamiliar to experienced
C/C++ programers using blaze, make, cmake. 

See the FS1 makefiles  for decent (hopefully) particulars.

Some other things to note:

#. The definitions vary between the Nano 33 BLE/IoT and the XIAO processors. **Beware**.

CLI
---

Follow the instructions:

`Seeeduino XIAO <https://wiki.seeedstudio.com/Seeeduino-XIAO/>`_

Arduino chips come in several flavors. Here we are using Arm -Core :index:`Arm` processors.

Download the Arduino IDE (here 1.8.15)

Under **File -> Preferences**

Into the **Additional Boards Manager URLs** enter:

"https://files.seeedstudio.com/arduino/package_seeeduino_boards_index.json"

**Tools -> Board -> Boards Manager**

Search/select **Seeed SAMD Boards** (see that it includes
Seeeduino XAIO M0, and install it. (here 1.21.1) Takes a beat.

The real trick is to start with the raw IDE and add the **Blink**
program. This shows the 'loop' is closed with respect to development.

Pin Outs
--------

..  code-block:: none
    :linenos:

    Pin Funcion Type Description
    1  D13          Digital GPIO
    2  +3V3 Power Out Internally generated power output to external devices
    3  AREF         Analog           Analog Reference; can be used as GPIO
    4  A0/DAC0      Analog ADC in/DAC out; can be used as GPIO
    5  A1           Analog ADC in; can be used as GPIO
    6  A2           Analog ADC in; can be used as GPIO
    7  A3           Analog ADC in; can be used as GPIO
    8  A4/SDA       Analog ADC in; I2C SDA; Can be used as GPIO (*)
    9  A5/SCL       Analog ADC in; I2C SCL; Can be used as GPIO(*)
    10 A6           Analog ADC in; can be used as GPIO
    11 A7           Analog ADC in; can be used as GPIO
    12 VUSB Normally NC; 
    13 RST          Digital In Active low reset input (duplicate of pin 18)
    14 GND Power Power Ground
    15 VIN Power In Vin Power input
    16 TX           Digital USART TX; can be used as GPIO
    17 RX           Digital USART RX; can be used as GPIO
    18 RST          Digital Active low reset input (duplicate of pin 13)
    19 GND Power Power Ground
    20 D2           Digital GPIO
    21 D3/PWM       Digital GPIO; can be used as PWM
    22 D4           Digital GPIO
    23 D5/PWM       Digital GPIO; can be used as PWM
    24 D6/PWM       Digital GPIO; can be used as PWM
    25 D7           Digital GPIO
    26 D8           Digital GPIO
    27 D9/PWM       Digital GPIO; can be used as PWM
    28 D10/PWM      Digital GPIO; can be used as PWM
    29 D11/MOSI     Digital SPI MOSI; can be used as GPIO
    30 D12/MISO     Digital SPI MISO; can be used as GPIO

Note: (12)can be connected to VUSB pin of the USB connector by shorting 
          a jumper Power In/Out

Logical
-------

Pins are "overloaded" in their ability; Use of some pins
precludes blocks of use.

..  code-block:: none
    :linenos:

    1  D13          Digital GPIO
    3  AREF         Analog  GPIO  Analog Reference
    4  A0/DAC0      Analog  GPIO  ADC in/DAC out
    5  A1           Analog  GPIO  ADC in
    6  A2           Analog  GPIO  ADC in
    7  A3           Analog  GPIO  ADC in
    8  A4/SDA       Analog  GPIO  ADC in; I2C SDA
    9  A5/SCL       Analog  GPIO  ADC in; I2C SCL
    10 A6           Analog  GPIO  ADC in
    11 A7           Analog  GPIO  ADC in
    20 D2           Digital GPIO
    21 D3/PWM       Digital GPIO  ; can be used as PWM
    22 D4           Digital GPIO
    23 D5/PWM       Digital GPIO  ; can be used as PWM
    24 D6/PWM       Digital GPIO  ; can be used as PWM
    25 D7           Digital GPIO
    26 D8           Digital GPIO
    27 D9/PWM       Digital GPIO  ; can be used as PWM
    28 D10/PWM      Digital GPIO  ; can be used as PWM
    29 D11/MOSI     Digital GPIO  SPI MOSI
    30 D12/MISO     Digital GPIO  SPI MISO

    16 TX           Digital USART TX; can be used as GPIO
    17 RX           Digital USART RX; can be used as GPIO

    2  +3V3 Power Out Internally generated power output to external devices
    12 VUSB Normally NC; 
    15 VIN Power In Vin Power input
    
    14 GND Power Power Ground
    19 GND Power Power Ground
    
    13 RST          Digital In Active low reset input (duplicate of pin 18)
    18 RST          Digital Active low reset input (duplicate of pin 13)

..

Libraries
---------

   `ArduinoJson library <https://arduinojson.org/?utm_source=meta&utm_medium=library.properties>`_ 

C++ Programming
---------------

The Arduino use C++11 standard, with exception-handling disabled. This does
not allow the "try/throw/catch" mechanism.

Arduino C++ does NOT honor namespace. Their use of map, ungarded, is
an example. It should have been called somthing like ardmap. 

Do not use using namespace std;

Do not use <iostream> -- it is massive.

You can use *#include <string>* and *std::string*. The STL string
environment has a few helpers:
overloaded to_string(X), where types of X include the integer and 
float families. Not that pretty. You can hack up a string format
routine.

The Arduino "sketch" implements Serial that can be better managed with a
small hex encoder; and std::string.

Arduino uses its own twisted make procedure. ANY file in the same directory
as the .ino file will be compiled and linked into the program. Be extremely
careful to keep this directory clean.

FlexSpec1 has a "FakeArduino.h" that allows compiling, and in many cases,
running this code under Linux. The Serial interface is not identical,
but some effort to allow its use is there.

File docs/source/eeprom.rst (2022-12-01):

EEPROM
======

The FS1 uses an 24FC256 I2C EEPROM module to store information. The module
is at I2C J11 and uses processor Pins 24 for SCL and 25 for SDA on Pin 25.
Its official address is 0x50. 

The EEPROM only supports 

We are using the AMC256 prom with ..math`256\times 1024 = 262144` bits
for 32768 bytes or ..math`32 \times 1024` pages.

We have less than 32 thingys to manage, so we allocate room for a JSON
string that is 1024 bytes long that mimics the process command for each main class.

The Flex_EEPROM module implements a simple load-leveling key/value system.
The key is the device name (user/system defined) and the value is a simple
ASCII only JSON string as sent to the device using the Patron Process
command, with RRR = No. The values are obtained by the Patron's Report
process.

https://ww1.microchip.com/downloads/aemDocuments/documents/MPD/ProductDocuments/DataSheets/24AA256-24LC256-24FC256-256-Kbit-I2C-Serial-EEPROM-20001203X.pdf

.. code-block:: python

    # Example of a pythonic image for the EEPROM. The placement depends
    # on the "flexspec" "toc" entry.
    eepromdefs = {"eeprom" : {"process" :
    {"flexspec" : {
        "owner"           : "indef",
        "contact"         : "indef",
        "serialno"        : "indef",
        "coderevision"    : "indef",
        "installdate"     : "indef",
        "updatedate"      : "indef",
        "toc"             : {
            "flexspec"        : "(0    ,1024)"
            "guidecamera"     : "(1024 ,1024)"
            "slit"            : "(2048 ,1024)"
            "fraunhofer"      : "(3072 ,1024)"
            "grating"         : "(4096 ,1024)"
            "camera"          : "(5120 ,1024)"
        }
    },
    "guidecamera" : {
        "vendor"          : "indef",
        "serialumber"     : "indef",
        "pixelsize"       : "indef",
        "lens1"           : "indef",
        "lens2"           : "indef",
        "ccdsum"          : "(1,1)",
        "slotoffset"      : "indef",
    },
    "slit" : {
        "vendor"          : "ovio",
        "serialno"        : "indef",
        "widthmicrons"    : "indef",
    },
    "fraunhofer" : {
        "baffleheight"    : "indef",
        "bafflewidth"     : "indef",
        "baffleoffset"    : "indef"
    },
    "grating" : {
        "name"            : "Thorlabs_500_600_25_0",
        "vendor"          : "Thorlabs",
        "catalogid"       : "GR25-0605",
        "length"          : "25.0",
        "height"          : "25.0",
        "thickness"       : "6.0",
        "lmm"             : "600",
        "cwave"           : "500",
        "blaze"           : "8.617",
        "dispersion"      : "1.65",
        "tcoeff"          : "8.0",
        "home"            : "indef",
        "offset"          : "indef",
        "other"           : "indef",
    },
    "camera" : {
        "vendor"          : "indef",
        "serialno"        : "indef",
        "pixelsize"       : "indef",
        "backfocus"       : "indef",
        "ccdsum"          : "(1,1)"
        "lensdesc"        : "indef",
        "lensaperture"    : "indef",
        "lensfl"          : "indef",
        "lensaperture"    : "indef",
        "tempsetting"     : "indef"
    }
    }
    }
    }

The FS1 has classes for various independent components. Some classes
are placeholders -- like the slit. Some refer to relativly inert elements
like the fraunhofer baffle. In roughly optical-axis order:

    #. flexspec - the details about the spectrograph itself. The "toc" (table of contents) lists starting offset and length for the 'page' by name. Accessing the structure by name allows the Postmaster to dispatch the initialization to each device's instance.

    #. guidecamera - important details known to the spectrograph to help inform the guide software (E.g.: Phd2)

    #. slit - Currently not selectable, establish on the bench. This will be an active class in future.
    #. fraunhofer - the geometry of the slit.

    #. grating - the details of the grating currently being used.

    #. camera - while controlled by other software (E.g.: libindi), the 'camera' (objective) lens, its backfocus, aperture, focal length do inform focus. At some point we hope to motorize this aspect.

The rest of the entries are self-explanatory. 

EEPROM Layout
-------------

The number of write cycles are important. We see the EEProm being used on a very 
infrequent basis. It will be consulted on each powerup/reboot of the Arduino.
The values are placed at locations within the EEPROM.

If page write is available use the beginTransmission(), ... write() ...
and endTransmission() calls. In our case, from 1 to 64 bytes may be written.

https://www.arduino.cc/reference/en/language/functions/communication/wire/begintransmission/

..

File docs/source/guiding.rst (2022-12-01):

FlexSpec 1 Guiding
==================

.. _rawguide1:



   Example 1-second raw guider exposure of M29, taken 2021-04-15, A. Rodda. Platesolved by nova.astrometry.net, image from ds9.



   Zoom into a guider image, showing astigmatism arising from the misalignment of the slit and guider mirror.

The :index:`FS1 guiding module` addresses matching wide field of view
surrounding the slit. This provides the opportunity to acquire the
target with an imprecise slew, plate-solve the image for precise
positioning and to increase the chances of having a brighter off-slit
star for alternative guiding. We applied the lens-makers formula to
create a compound 2-element "transfer lens" solution.  The equation

.. math::
    \frac{206264.8}{\tt{fl}\times 1000} = \frac{\tt{Magic Number}}{1 \mu{m}}

yields the ":index:`Magic Number`" in units of arc-seconds per micron for a
telescope with a focal length of :math:`{\tt{fl}}` in units of mm. This
equation allows computing/planning the :index:`slit width;matching` in terms of
arc-seconds of seeing. Matching the slit width to the OTA magnification
and seeing is critical to acquire the best signal, limit the sky
contributions and to mitigate the effects of atmospheric refraction
(see Parallactic Angle and Rotation \ref{sec:Rotator}.

In imaging, multiplying the number by the pixel size in microns,
yields the arc-seconds per pixel. Further multiplication by the size of
the chip yields the total field of view for the image. This number
should be permanently affixed to the OTA.

.. index:: 
   single: calculation;pixel size
   single: calculation;slit width

The :index:`lens makers equation`:

(DIAGRAM)

.. math::
    \frac{1}{fl} = \frac{1}{s_{1}} + \frac{1}{s_{2}} \label{E:LensMakersEquation}

is chained together for each lens in the set to match the computed
platescale on the slit to the chip size of the camera.

(EXAMPLE IMAGE).

Preliminaries
-------------

Take a small series :index:`calibration exposures`, flats, zeros and
darks for the guide camera. :index:`FS1 slit carousel` has one position
filled to serve as a general :index:`shutter` for dark exposures. 

#. Take zeros and darks, flats and make masters
#. Solve for defects: :math:`(x,y)`.
#. Slew to field
#. Take a few long exposures (10sec?) to reach mag 15
#. Correct images darks/flats/defects
#. Identify main stars and platesolve.
#. Illuminate the slit from behind.
#. Solve the slit position (:math:`y = mx+b`)

For the slit:

#. The slit has rotated.
#. Position a point-source onto the 'old' best position.
#. Science image.
#. Solve the 'Y' offset of point source.
#. Recalculate the guide :math:`(x,y)` for point source to put the dispersion axis back onto original points.

Science Camera:

#. Take zero/dark/flats
#. Determine the defect map :math:`(x,y)`.
#. Determine an optimal position :math:`(y)` for dispersion axis based on defects.
#. Record the position.

PHD2 Guiding Setup
------------------

A handy videos" 

#. `Christopher Kovacs PHD2 Guiding <https://www.youtube.com/watch?v=zA2OrhXik6g>_`

#. `Christopher Kovacs Kstars/Putty <https://www.youtube.com/watch?v=odChu13_5RM>_`

#. Start Kstars
#. Under Tools->Ekos
#. Edit the profile.

#. The profile should be setup with PHD2 and the path to the server.

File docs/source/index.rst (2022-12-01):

..
    extend sphinx-latexpdf docker container with the Dockerfile in the
    root of this repo
   
    apt-get update
    apt-get -y install gcc
    pip3 install numpy
    pip3 install astropy[all]
    pip3 install pandas
    pip3 install bokeh
   
    docker run -it --rm -v /home/git/external/FlexSpec1/docs:/docs \
                        -v /home/wayne/anaconda3/lib:/opt/lib \
                           sphinxdoc/sphinx-latexpdf /bin/bash
   
    docker run -it --rm -v /home/git/external/FlexSpec1/docs:/docs \
                           sphinxdoc/sphinx-latexpdf-fs1 make html

    docker run -it --rm -v /home/git/external/FlexSpec1/docs:/docs \
                        -v /home/wayne/anaconda3:/opt/lib \
                        -e PYTHONPATH=/home/wayne/anaconda \
                           sphinxdoc/sphinx-latexpdf make html latexpdf

    docker run -it --rm -v /home/git/external/FlexSpec1/docs:/docs \
                        -v /home/wayne/anaconda3/lib:/opt/lib \
                           sphinxdoc/sphinx-latexpdf /bin/bash

    browser build/html/index.html
   
    /home/wayne/anaconda3/bin
    /home/wayne/anaconda3/condabin

INTRODUCTION
============

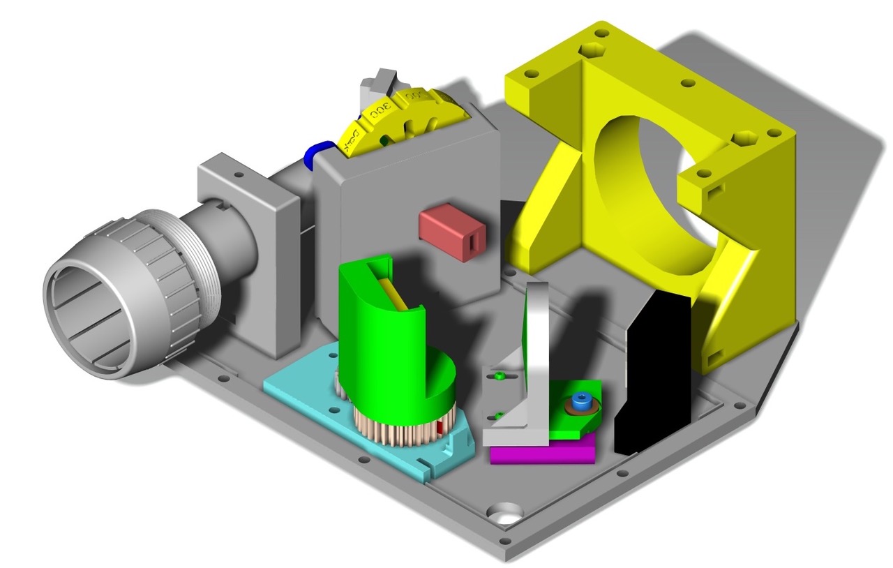
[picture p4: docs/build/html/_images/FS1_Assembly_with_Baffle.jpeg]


   CAD Layout for optical components of the FlexSpec 1.

The spectroscopist wants what they want. The spectrograph gives what
it will. One must strike the Faustian bargain that may only be paid
with the coin of credibility. Choose wisely.

The FlexSpec1 (FS1) spectrograph grew out of a segmented analysis of
the entire impact on a spectrum starting with the Source signal; through a
telescope's optical tube assembly (OTA); through the focal plane;
through the spectrograph; and into the sensor. This article limits all
variables from the Source to the OTA to one parameter: the Parallactic Angle. 

to those involving the impact of the atmosphere
(parallactic angle), the effective focal length of the main OTA, and
relationship of the OTA to the device injecting a calibration lamp
signal (Herein the Kzin ring).

Only the flux distortions taking place between the Source (a Star, Planet,
Calibration Lamp) are considered up to the

Ramifications of 3D printing leading to FlexSpec 1 (FS1): 
Introducing the Flexible Spectrograph I
Small Telescope Spectrograph.

This is documentation, the project and our aspirations for developing
a science data quality 3D spectrograph that is 'Flexible'.

It is a continuous in progress. Bear with us. Better yet, collaborate with us.

The STL and STEP files, EDA and CAD files and the software
may be cloned from the `FlesSpec1 Github Repository <https://github.com/The-SMTSci/FlexSpec1>`_ here.

.. toctree::
   :maxdepth: 3
   :numbered:
   :caption: Contents:

   abstract
   flexspec1
   openquestions
   eeprom
   kzin
   ovio
   parallacticangle
   optics
   experiments
   overview
   physics
   mathematics
   guiding
   protocol
   controls
   communication
   serial
   software
   postmaster
   cad
   electronics
   arduino
   documentation
   docker
   bom
   callamps
   outstanding
   history
   references
   youtube
   printer
   merlin
   url

Indices and tables
------------------

* :ref:`genindex`
* :ref:`modindex`
* :ref:`search`

.. 
   docker run -it --rm -v /home/git/external/FlexSpec1/docs:/docs sphinxdoc/sphinx-latexpdf-fs1 make html latexpdf

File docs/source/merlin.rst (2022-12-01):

MERLIN GCODE Tricks
===================

GCode "Gerber" code is widely used in Computer Numerical Code (CNC) machining.
Most 3D printers us Merlin's implementation. Full documentation is elsewhere.

Here are a few practical tips:

We use `Octoprint <https://octoprint.org/>`_ to interface the printer
to the recommended Raspberry Pi 3B, 3B+ or 4B computer. This is a
35USD simple solution, web based and easy to use. This is all open-source
code.

Make sure to enable autoscroll on the terminal.

The basics of GCode include a "letter" command and parameters.
Comments are enclosed in parenthesis (this is a comment).

OctoPrint and slicer programs allow users to create *scripts* to prepend
or append to the produced gcodes. Octoprint allows additinal scripts
(or the only ones) to be stored within the Octoprint computer. This
allows fine-tuning of gcode output to fit genaral or specific (one time)
needs.

Hand gcode scripts include one to make a small side print prior to
starting (test feed, bed adhesion); to raise/move the print head/bed
after the print -- etc.

M503 - dump the salient printer internal values. A screen dump from
OctoPrint via the Terminal tab::

    Send: M503
    Recv: echo:Steps per unit:
    Recv: echo:  M92 X81.00 Y81.00 Z400.50 E94.30
    Recv: echo:Maximum feedrates (mm/s):
    Recv: echo:  M203 X450.00 Y450.00 Z5.00 E25.00
    Recv: echo:Maximum Acceleration (mm/s2):
    Recv: echo:  M201 X3000 Y3000 Z100 E3000
    Recv: echo:Acceleration: S=acceleration, T=retract acceleration
    Recv: echo:  M204 S1000.00 T800.00
    Recv: echo:Advanced variables: S=Min feedrate (mm/s), T=Min travel feedrate (mm/s), B=minimum segment time (ms), X=maximum XY jerk (mm/s),  Z=maximum Z jerk (mm/s),  E=maximum E jerk (mm/s)
    Recv: echo:  M205 S0.00 T0.00 B20000 X10.00 Z0.40 E1.00
    Recv: echo:Home offset (mm):
    Recv: echo:  M206 X0.00 Y0.00 Z0.00
    Recv: echo:PID settings:
    Recv: echo:   M301 P33.41 I1.47 D189.27
    
Initial Tests
-------------

The initial testing should include printing a known good piece, and fine
tuning the M92 codes. To do this download a block like:

`CHEP <https://www.youtube.com/watch?v=UUelLZvDelU>`_

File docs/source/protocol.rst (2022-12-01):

Remote Protocol
===============

The control structure is being developed in a platform agnostic network
neutral fashion leveraging web applications (web apps) via bokeh and
other tools. The idea is the UI side maintains a set of shared variables
with the FlexSpec C++ classes. This shared subset of UI/C++ variables
forms a **contract** between the two environments. Here we will refer
to the classes outside of the FlexSpec C++ classes as the **client**.
The client states what internal **state-of-affairs** the FlexSpec C++
class is to achive and maintain. The FlexSpec C++ class may come
close -- as in the case of converting a wavelength to a rotation
of the grating. It will be the case that the specified wavelength
will fall between two step intervals of the motor. In this
case, the FlexSpec C++ will achieve its closest value, and
report that back to the client; the client will then update
its state-of-affairs to reflect that action. 

The state-of-affairs will consist of pure ASCII characters to
be shared between any client and the FlexSpec C++ class using
a Pythonic JSON string image.

The JSON (**J**ava**s**cript **O**bject **N**otation) is referred to
as **data** in the literature. Python uses **dictionaries** that
are, essentially, JSON like constructs. C++ on the other hand 
does not have a nested key/value container in the Standard Template
Library. We carefully use a subset of the JSON overall capabilities
to transfer requests from the client, and to return the internal
state-of-affairs from the FlexSpec C++ class.

The Bokeh web-app UI is used. This avoids installing code on the
user's machine. The web-app relies on a **dispatch** server to support
a bokeh server running on a Raspberry Pi. A RPi may be installed on
one or more OTAs for the management and control of local (to
the pier/mount/ota) devices. This is where the FlexSpec stops. 

The rest of scheduling/cameras/slewing related activities are left to
management by LibIndi/EKOS in the usual fashion.  The local
Bokeh/PostmasterServer are a peer in an asynchronous distributed
network of peers. Any SBC/Desktop computer with a decent operating
system may be used for the server. The ODroid, BeagleBone, Intel NUC
etc. Some SBC :index:`SBC;Configuration` configuration will be
required.

Arduino class devices are designated as an SBM is a "Single Board
Microcontroller".

This approach sticks with the Arduino control system (boots out of the
box) and does not use an after-marker RTOS or PyCharm.

The essential parts:

- The actual hardware at the interface of the SBM and the real world,
  where the if/then/else/switch/maths part is next to the
  hardware. Timing may exist here.

- The logical element within the Arduino for a part: A 'StepperMotor' may
  have several ways to do things, there may be several different steppers
  in a device. Handles the commands and is a communications terminus
  or originator of status etc back to its manager.

- The Raspberry Pi/Odroid/Linux box that owns the serial wires. Actual
  wires.

- The user interface:
     - People via interaction a browser with buttons etc...
     - A controller program like a scheduler
     - (both at the same time)

One hard part is the timing required. We don't have any real sense
of a "timer". We have hacked up something to help, but that control
loop gets complicated with more than one set of things to do.

The other main division is in how messages flow.

- A message shall only be a JSON structure. The structure will be
  created by a program and therefore checked before being sent. This
  requirement removes all the checking requirements in the
  Arduino. The JSON message will be a single string of ASCII
  characters consisting divided into two classes of characters: Case
  1) special - the braces, colon, comma and double quote mark {}:,"
  Case 2) The characters A-Za-z0-9._ and noting else.

**Case 1** are filtered when messages are parsed. This makes matching the close
     brace to the open brace very small in the Arduino.
**Case 2** Means any illegal character -- that have a remote possibility
     of occurring due to a bit-flip in coms, can act as a trigger to reset.

A JSON structure is a "dictionary" (special collection or set) of a
  "key" and a "value". A key is restricted to being only a quoted
  string and a value may be one of three things: a quoted string,
  ASCII integer representation, float in the form of
  whole-dot-fraction expressed.

The Serial communications assumes more than on SBM on a wire pair. 
All listen to the wire and parse a single JSON dictionary that matches
their name. The SBM parses this dictionary and dispatches any enclosed
value JSON dictionaries to each "widget". The widget is responsible
for understanding and acting on the content of that dictionary.
A Key is considered a class of command and its values are considered
the parameters for that action.

This next part is a trick.

There will be two "mirrored" classes: Python for the Raspberry Pi
and C++ for the SBM.

The class (Python) in the Raspberry Pi has to mirror the class in the
Arduino exactly. This allows them to communicate in their own agreed
upon way to assure proper operation. This requirement alleviates
the need for a universal grammar or command set. 

The 'format' of the message will be 1) JSON BUT 2) the content is left
up to both sides of that class.  The Python will have Bokeh/GUI
stuff. The Arduino implements all the tedious logic to make things act
and/or move. The paradigm is one of a Navy Captain and the Chief of
the Boat: The Captain knows he wants to make a certain speed to
a target and no idea how that happens. He 'orders' the Chief
to make 15 knots NNE. The Cheif tells the engine room to make
a certain number of 'revolutions'.

The GUI user does not want to think in terms of stepper-motor
steps, directions. They want to move to a logical position.
The Arduino receives a JSON key/value pair that might say --
in this scenario -- { ... "speed" : "23[knots]" ... } and
parses the value as it sees fit. The units may be implicit, as
the two classes understand how that message's value needs to
be handled.

The Raspberry Pi Python class communicates with the 'user'
(person/algorithm). In this case a Python web-app built on Bokeh, or
will simply accept and pass-thru messages from an algorithm user. It
lives on a Raspberry Pi, and has lots of program space to do all the
logic and format checks to guarantee the messages sent to the SBM is
correct.  (Remember remove checks from the Arduino to the degree
possible).

The Raspberry Pi owns the 3.3V rx/tx serial lines, I2C, BLE and GPIO
ports.  This means the PostmasterServer provides the single access
point to all classes/programs the electrical system. It utilizes a
Unix socket protocol, and permits connections from multiple GUI
clients. Devices, like an Arduinoa accepts
and queues messages and routes them to "devices" implemented
as C++11 classes.

In the code repository the Slit may look like:

FS_Slit.h
FS_SLit.cpp
FS_SLit.py

They will have dependencies in other classes within the architecture,
to handle the Bokeh (Python) and the messaging (Python and Arduino).

Summary:
--------

The controls/sensors may be part of the Raspberry Pi itself, using a
separate RS-232/I2C/Wireless/Ethernet channel to the physical bits;
They may go through RS-232/I2C/BLE to a Arduino SBM. Tying these
together will be in Python/C++ on the Raspberry Pi. Doing the work is a
problem left somewhere else -- but required to use this communications
scheme.

Differences with ASCOM:

We do the GUI parts inside the chain, and do not rely on templates
as shims between components. This makes fast/direct coding possible.

Kzin Ring Example
-----------------

The Kzin ring example:



   The Kzin ring has the ability to turn on one or more of the lamps within its purview as needed. Here NeAr, Osram (Argon only), H-Alpha (LED), O[III] (LED), Flat (Compo of lamps) and Blue (additional LEDs) may be chosen. The yellow area is a debug mode window showing the text to be sent by serial port to the registered LED.

.. code-block: none
   :linenos:

    {"Kzin": 
       {"Process": 
          {"near": 1, "osram": 0, "halpha": 1, "oiii": 0, 
           "flat": 0, "augflat": 0}
       }
    }
    
The nested-dictionary is nested inside a distribution to the "Postmaster"
that owns the spectrograph with the Kzin ring. The "Postmaster" on the
particular Arduino dispatches to an instance of a Kzin class with
the name (Kzin) the class sends the settings to to the class using
the "Process" method. The fine details of "Process" are implemented
to set the internal state and do what is necessary to conform that internal
state to the operation of that ring. In other words, if 'osram' had been on
at the time "Process" was called; it will be turned off. I 'near' was
off it is turned on -- all within the context of this one 'command' to
the Kzin ring.

The details of routing are not shown, as the Bokeh class only contributes
this message and that is the text we see.

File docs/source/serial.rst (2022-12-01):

Serial Communication
====================

The ACMn device is expected to implement ITU V.250 (Hayes 302) protocols,
though that is seldom the case. We want the /dev/ttyn type of
interface.

CDC/PSTN

Raspberry Pi
------------



   Reference for GPIO pins. (Raspberrypi.org)

Make sure serial is enabled via the **raspi-config** file.

.. code-block:: none
   
   sudo raspi-config
   Would you like a login shell to be accessible over serial? no
   Would you like the serial port hardware to be enabled? YES
   Save and reboot.
    
.. code-block:: none
   
   minicom -b 115200 -o -D <Port_Name>

<Port_Name> is either /dev/ttyAMA0 or /dev/serial0 

Connect pin 14 and 15 (loopback) test.
minicom or similar will work.

To check what ttys are available (Astroberry example here):

.. code-block:: bash

   dmesg | grep enabled | grep -o -- "tty[0-9]\+"

Get a terminal emulator for assistance with development.

.. code-block:: bash

   sudo apt install putty

Run PuTTy, and the program starts a small GUI. In the case
of the Arduino IDE, use the Tools -> Serial -> Monitor
and, in one case, the port is "/dev/ttyACM" and the rate
is "115200".

Save the session. 

"Load" a named session. Then change the font FreeMono font-size to 14,
background (light green to sorta imply Arduino), text color to black,
cursor to black

You can change the font sizes, colors etc
via the PuTTy GUI and save with the session. Good idea to
use different color as needed.

Attach a small Arduino, running a script to print "Hello World"
every second, and you should output. This verifies a "closed
loop" solution has been achieved with PuTTy!



   Screenshot of Putty, under Ubuntu 18.04 Xfce. Note: the Category column -- where Window Color, Fonts etc may be found and changed. Note: Saved sessions offer the ability to name a session. One may achieve a pleasing appearance by selecting TitanSerialACM0_Arduino, then Load; change the options and resave.

WARNING:

COMMON VOLTAGES FOR PINS ON Small Board Computers range across
1.8, 3.3 and 5 VOLTS. MIXING SIGNALS CAN PERMANENTLY DAMAGE
HARDWARE.

FlexSpec software supports I2C and RS-232 and RS-485 as the communication
spec. I2C is a common scheme between boards located in very close
proximity. RS-485 is a differential signal scheme, range just over 1
kilometer. RS-485 wraps a 0-5V signal within a common-mode noise
voltage range of -7 to 12 V ( -7 to (0:5 +7) = 12 V). Long hauls,
multidrop capability and noise immunity are hallmarks of the RS-485
protocol.

RS232, ( Telecommunications Industry Association TIA-232-F)

* 0 (space)	Asserted	+3 to +15 V    "Computer zero"
* 1 (mark)	Passive	-15 to -3 V    "Computer one"

There is a "hysteresis" of 6V absolute (-3 to 3) between valid
signals to differentiate noise.

The maximum voltage range is from -25 to 25 volts.

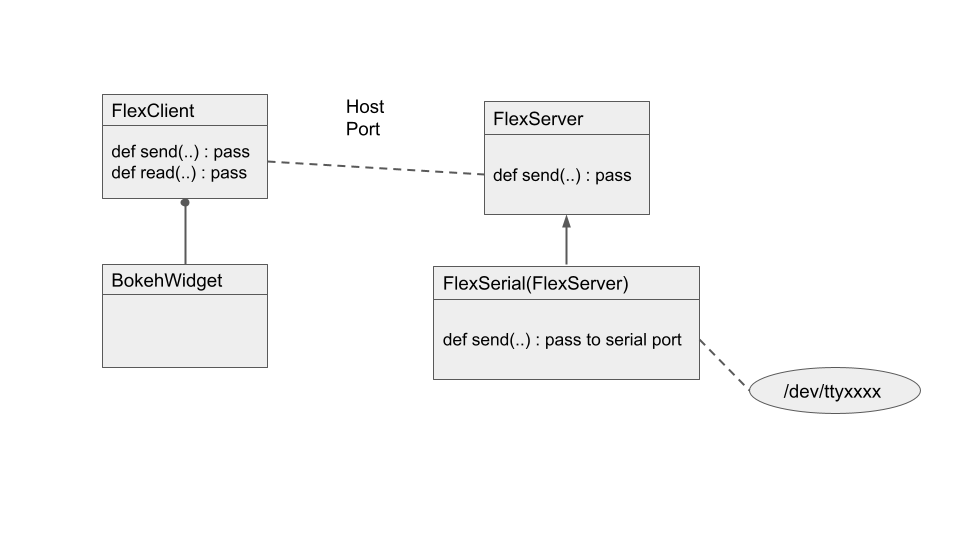
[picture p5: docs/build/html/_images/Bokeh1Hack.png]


The Bokeh widget uses a "has-a" relationship to one or more
PostmasterServers. The PostmasterServer may be local to same
machine or remote.  The message is passed to any subclass -- here a
FlexSerial class which owns the interface to it's local machines
serial port where Arduino/other SBMs reside.

..
    -----------------------------------------------------------------------------
    LGDehome 10PCS Max485 Chip RS-485 Module TTL to RS-485 Module for Raspberry Pi
    B08DN47BHR

    SystemBase - Made in Korea - USB to 1port RS422/RS485 Terminal
    Block(5pin TBL) Serial Converter, Cable Length 1.97ft(0.6m), Latching
    Applied USB 2.0, USB to RS422/485 Serial Converter (BASSO-1010UC)

    -----------------------------------------------------------------------------

    NOYITO TTL to RS232 Module TTL RS232 Mutual Conversion Module Serial
    Level Conversion to SP232 for MCU, ARM, FPGA, Arduino, etc. TTL Serial
    Port communicates with RS232 Level Device.

    Implements CTS and RTS. (MAX3232)
    -----------------------------------------------------------------------------

    https://opensource.com/article/20/5/tio-linux  mknod trick

Linux Minicom
-------------

A rough analog for PuTTY for Unix, old as the hills of Allentown.

..

    Disconnect the adapter, turn off the Arduino.
    sudo -s # change terminal to red!
    dmesg -C # clear the dmesg buffer
    dmesg | grep USB
    #NOTHING which is good
    attach the adapter
    dmesg | grep USB  # shows lots, find the /dev/XXXXXXX and use the XXXXXXX
    minicom -s  # -s is vital
    ... starts gives a config screen...
    # in the screen, scroll down to serial
    Set to dev to /dev/XXXXXXX
    baud to desired, 8N1
    hardware control to yes
    software control to no
    ... exit... setup

Now, start arduino, and you should see stuff.
Do your thing.

#. **Note** from the keyboard Ctrl-A is the leadinto commands

Related Videos
--------------

`Christopher Smith Minicom Video Linux <https://www.youtube.com/watch?v=AzX_Ni8TM0Y>`_

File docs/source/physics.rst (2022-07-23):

vPhysics
========

This section contains the basic mathematical underpinnings used in our
analysis of the basic DIY spectroscope.

The optical :index:`sign conventions` used here follow Schroeder's (1987)
"Cartesian" approach. The plane for the optics ("wen/mirror surfaces")
are in the XY plane, the optical axis follows the Z axis.  Along the Z
axis, rays pass from the negative (lesser) to right
(greater). Reflections reverse the sign. (I.e.: photons move in the
positive direction along the Z axis.)

There are at least 6 dispersion techniques to consider:

- (1) Fresnel (nearfield),
- (1) Fraunhofer (slit) diffraction,
- (2) Reflection and transmission diffraction gratings,
- (2) Prisms and a grism (combination prism/transmission grating).

A lot of the mathematical manipulations used here are accessible via
the `Wolfram Alpha web site <https://www.wolframalpha.com>`_ , freely accessible and with paid
subscriptions.

BOTE Computation
----------------

To assist with basic design and to develop intuition, "Back of The
Envelope" :index:`BOTE;Back of The Envelope` computation is in
order. Astronomers utilize the "Centimeter Gram Seconds" (CGS)
system. Here are a few guide pointers:

#. Use the same units, here centimeters;
    - :math:`5 \times 10^{-5}` cm for green light. :math:`5 \times 10^{-5}` cm for blue and :math:`6 \times 10^{-5}` cm for red. We use 300 and 600 l/mm gratings and the math cancels!
    - Translate grating :math:`l/mm to` :math:`l/cm`

#. Remember sign conventions, and get the right equation.
#. Follow the general spectrograph equation chain. Slit/grating/sensor.

Light
-----

A wavelength is a cycle, its length is a function of the energy of the
associated photon. An image has a 'wavefront' and that wavefront has a
quality, expressed in fractions of a wavelength (variation of 1/10th
of a wavelength :math:`2\times\pi/10 = 0.328` (360 degrees for a full
cycle) amounts to a shift of around 36 degrees! A lot of error. Using
a 'folding' mirror :index:`mirror;folding` adds error. This same
wavefront error seeps in with irregular coatings and lens surfaces.  It
creeps in with the parallelism agreement between the front and back of a
lens; with the co-alignment of lenses; and with the flatness of a
grating's plane.

The Behavior of Lenses
----------------------

In theory, lenses work well. In practice there is the issue of the
agreement between the curve at the front of the lens and that at the
back of the lens (a wedge or a prism-astigmatism effect). The distance
between a surface at the edge adds additional chances for
dispersion of the light as it passes through the lens. The cheaper the
lens the more likely the lens has issues.

Glass refracts, deferentially, as a function of energy (wavelength).

Lens Makers Equation
--------------------

The general form of the :index:`lens makers equation`:

.. math::
    \frac{1}{f} = (n-1) \left[ \frac{1}{R_1} - \frac{1}{R_2} + \frac{(n-1)d}{n R_1 R_2} \right]

where:

- :math:`n`  is the index of refraction,
- :math:`f`   the lens' focal lengths,
- :math:`R_1` is the **radius of curvature** of the surface towards the object,
- :math:`R_2` is the radius of curvature of the surface towards the sensor, and
- :math:`d`   is the thickness of the lens

See `Wikipedia's Lens Makers Equation <https://en.wikipedia.org/wiki/Lens#Lensmaker's_equation>`_.

Thin Lens Equation:

In practice the thin lens equation:

.. math::
   :label: thinlens

   \frac{1}{f} = \frac{1}{S_1} + \frac{1}{S_2}

Snell's Law
-----------

.. math::
    \frac{\sin\theta_2}{\sin\theta_1} =  \frac{n_1}{n_2}
     =\frac{v_2}{v_1}

.. math::\frac{n_1}{n_2}

where:

TODO: This needs to be verified the image names match the labels.

- :math:`\theta_x` are the angles involved.
- :math:`n`  is the index of refraction,
- :math:`v`  is the speed of propagation

Reflection
----------

The :index:`OVIO slit` is not an air slit. Internal reflection
tends to scramble the beam at this point.



   Total reflection (mirror).



   Reflection from a glass surface, portion of the I:subscript:`0` is lost.



   Exit angle refraction. (The other side of the slit substrate.)



   Total internal reflection.

TODO: refine this section.

The `calculator <http://hyperphysics.phy-astr.gsu.edu/hbase/phyopt/freseq.html>`_ at:

helps to calculate the pertinent values. A f/5 beam is the arctan(1/5)
= 11.30 degrees. Divided by 2 gives 5.65 degrees -- from the optical
axis to the side of the converging cone. With n\ :subscript:`1` =
1.0001 (air) and n\ :subscript:`2` = 1.53 (BK7-ish).

s-polarized:

.. math::
    R_\mathrm{s} = \left|\frac{Z_2 \cos \theta_\mathrm{i} - Z_1 \cos \theta_\mathrm{t}}{Z_2 \cos \theta_\mathrm{i} + Z_1 \cos \theta_\mathrm{t}}\right|^2

p-polarized

.. math::
    I = I_0 \frac{ 1+\cos^2 \theta }{2 R^2} \left( \frac{ 2 \pi }{ \lambda } \right)^4 \left( \frac{ n^2-1}{ n^2+2 } \right)^2 \left( \frac{d}{2} \right)^6     

TODO: https://en.wikipedia.org/wiki/Total_internal_reflection#/media/File:Total_internal_reflection_by_fluorescence.jpg

Using the `Shott Pocket Catalog <https://www.schott.com/d/advanced_optics/c36214d9-13c4-468c-bf40-8d438b89f532/1.30/schott-optical-glass-pocket-catalog-jan-2020-row.pdf>`_ 

A point source (star) receives information from the entire aperture with
a slight distortion due to its off-axis relationship. For spectroscopy,
careful centering and alignment of the 'target' position on the slit
onto a co-aligned optical axis keeps the noise symmetric. Off-axis
star means asymmetric line profiles at the sensor. Slight, but there.

In considering the `OVIO <https://en.ovio-optics.com/media/pim/assets/DocumentsPDF/std.lang.all/2-/en/Notice-Ovio-204012-EN.pdf>`_ slit with a beam consisting a pencil of rays
(bundle of rays -- each with a different approach angle to the
surface). Using the above equations it is easy to see that the f/ratio
is altered significantly as each ray enters, passes, and exits the
slit's substrate. There is a condition where internal reflection adds
an additional ray with changed geometry.  This amounts to noise in the
system. It is not a true caustic.

Grating Equation
----------------

.. math::
    :label: grating

    \frac{m\lambda}{d} = sin(\alpha) \pm sin(\beta)

where :math:`\lambda` is the wavelength, :math:`\alpha` is the angle
of incidence, :math:`\beta` is the diffracted angle (the dependent
variable of real interest). The sign :math:`\pm` is positive for
reflection gratings and negative for transmission grating. The angle
:math:`\phi = |\alpha| + |\beta|` defines the main geometry of the
system.

Spot Size and Slit Selection
----------------------------

In practice, the focal length drives the platescale :eq:`pixelscale`
and aperture drives resolution :eq:`RayleighEquation`.

In general, the :index:`spot-size` is independent of the aperture, and
wholly dependent on the focal length. Since f/ratio is a derived value
-- equation :eq:`pixelscale` bypasses the aperture and gives a result
as a fraction of an arcsecond per micron at the focal plane:

.. math:: \frac{206204.8}{fl\times 1000} = \frac{x^"}{1 \mu{m}}
   :label: pixelscale

This is a elementary school ratio problem: where :math:`206204.8` is
the number of arc-seconds in a radian; :math:`fl` is the focal length
in mm (traditionally stated) and multiplied by 1000 to turn into
microns; :math:`x^"` is "x" in arc-seconds; the goal of :math:`1 \mu{m}`
relates to both pixel size and slit width.

In spectroscopy, the Rayleigh equation :eq:`RayleighEquation` provides
a critical estimate of the ability to separate the light from two
close objects.

.. math:: \theta = 1.22\;\frac{\lambda}{D}
   :label: RayleighEquation

where :math:`\theta` is the resolution IN RADIANS; :math:`1.22` is the
first Bessel J coefficient; :math:`\lambda` is the wavelength in units
of D; and :math:`D` is the diameter of the aperture. For
back-of-the-envelope estimates, use 5e-5 (:math:`5\times 10^{-5}`) as
the wavelength in [cm] and express D in matching units [cm].

**Observation:** The width of the slit dominates resolution within the
spectroscope. The aperture requirement stresses the need for flux over
resolution. A short focal length stresses the need for a small "spot
size", allowing a smaller slit width; in turn driving higher resolution.

The so-called 'diffraction limited' requirement of one arcsecond for
stations deep in the atmosphere only requires an aperture of around
12.58 cm (4.95 inches). This is all that is satisfy most amateur
needs under above average seeing conditions.

Sellmeier Equation
------------------

The :index:`Sellmeier Equation`, uses an empirical equation to model the
dispersion of light in medium with a given refractive index.

Values may be found at [Polyanskiy-2021]_: `Refractive Index Database <https://refractiveindex.info/>`_

.. math:: n^2(\lambda) = 1 + \sum_i \frac{B_i \lambda^2}{\lambda^2 - C_i}
   :label: sellmeier1

In practice, a small handful of empirical constants determines a
workable solution to path-times for lenses:

.. math:: \lambda = 1 + \frac{B_1 \lambda^2 }{ \lambda^2 - C_1}
      + \frac{B_2 \lambda^2 }{ \lambda^2 - C_2}
      + \frac{B_3 \lambda^2 }{ \lambda^2 - C_3}
   :label: sellmeier2

Coefficients may be had from several sources:

    +----------+---------------------------+
    |B_1       |1.03961212                 |
    +----------+---------------------------+
    |B_2       |0.231792344                |
    +----------+---------------------------+
    |B_3       |1.01046945                 |
    +----------+---------------------------+
    |C_1       |6.00069867 x 10^ 3 microns |
    +----------+---------------------------+
    |C_2       |2.00179144 x 10^-2 microns |
    +----------+---------------------------+
    |C_3       |1.03560653 x 10^ 2 microns |
    +----------+---------------------------+

Scattering
----------

In optical spectroscopy the wavelength ranges from 3300-12,000 Angstroms
or .33 to 1.2 microns. Particles or defects in the optics may be
modeled by :code:`\sigma = 2\pi\r/\lambda`. Rayleigh scattering occurs when 
:code:`\sigma << 1` and :code:`\sigma << \lambda/10`. 

..  math::
    :label: RayleighIntensity

    I &= I_0 \frac{ 1+\cos^2 \theta }{2 R^2} \left( \frac{ 2 \pi }{ \lambda } \right)^4 \left( \frac{ n^2-1}{ n^2+2 } \right)^2 \left( \frac{d}{2} \right)^6

<ref>Seinfeld, John H. and Pandis, Spyros N. (2006) ''Atmospheric Chemistry and Physics, 2nd Edition'', John Wiley and Sons, New Jersey, Chapter 15.1.1, {{ISBN|0471720186}}</ref>

..  math::
    :label: RayleighScattering

    \sigma_\text{s} &= \frac{ 2 \pi^5}{3} \frac{d^6}{\lambda^4} \left( \frac{ n^2-1}{ n^2+2 } \right)^2

``Siegel, R., Howell, J.R., (2002). [https://cds.cern.ch/record/1505325/files/9781439805336_TOC.pdf ''Thermal radiation heat transfer'']. p. 480. New York, NY: Taylor & Francis. {{ISBN|1560329688}}``

Lambertian Reflection:
----------------------

One :index:`calibration lamp` method involves flooding the guider/slit chamber with
light from an off-axis lamp. Experiments (Rodda/Yeager) showed variation
in lamp placement had a significant impact in calibration line placement
on the spectrum. Here is the simple case of light from a bulb radiating
outwards. If the lamp is replaced with a patch of the reflecting area
inside the chamber; and considering all contributions from the entire
area of the chamber -- it is easy to see where the off-axis contributions
originate.  TODO Add reference to the 'Greg's device'.

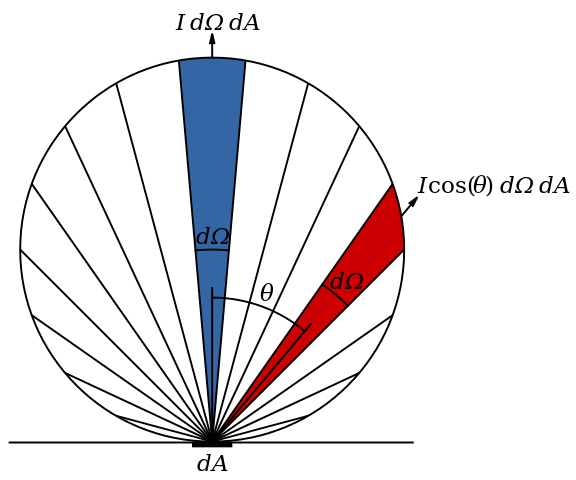
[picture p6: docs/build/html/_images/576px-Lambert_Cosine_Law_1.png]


   Relationship of reflection to solid angle :math:`\Omega`. (Wikipedia)

.. math:: 
    :label: Lambert-1

    F_{tot} &= \int\limits_0^{2\pi}\;\int\limits_0^{\pi/2}\cos(\theta)I_{max}\; \sin(\theta)\;\mathbf{d}\theta\;\mathbf{d}\phi \\
    &= 2\pi\cdot I_{max}\int\limits_0^{\pi/2}\cos(\theta)\sin(\theta)\;\mathbf{d}\theta \\
    &= 2\pi\cdot I_{max}\int\limits_0^{\pi/2}\frac{\sin(2\theta)}{2}\;\mathbf{d}\theta

Using `Wolfram Alpha web site <https://www.wolframalpha.com>`_ :

.. code-block:: none

    integrate sin (2x / 2) dx from x = 0 to pi/2

.. math:: \int_0^{\pi/2} sin (2x / 2)\; \mathbf{d}x = 1

Thermal Expansion
-----------------

In general the degree of thermal expansion is :math:`\propto` inverse
of the melting point. In practice the ODE

.. math::
    :label: ThermalExpansionODE

    \alpha_{L} = \frac{1}{L}\; \frac{\mathbf{d}L}{\mathbf{d}T}

where :math:`L` is the length :math:`T` is in units of temperature.
FlexSpec 1 uses MKS, so coefficients here are in :math:`\mu{m}/m/K`.

.. csv-table:: Material Thermal Coefficients
    :header-rows: 1
    :widths: 50,15
    :align: left

    "Standard Material","Coefficient"
    "Aluminum",23.1
    "Brass",19
    "Carbon steel",10.8
    "Invar",1.2
    "Douglas-fir",3.5
    " "," "
    "3D FILAMENTS","3D FIBER COEFFICIENTS"
    "ABS",90
    "ASA",98
    "Carbon Fiber Filled",57.5
    "Flexible",157
    "HIPS",80
    "Metal Filled",33.75
    "Nylon",95
    "PETG",60
    "PLA",68
    "PVA",85
    "Polycarbonate",69
    "Polyproplyne",150
    "Wood Filled",30.5

`Simply3D Table <https://www.simplify3d.com/support/materials-guide/properties-table/>`_ has lots of properties related to 3D printer filaments.

TODO: Young's Modulus.
Same issues in every spectrograph

Things we did to minimize.

Binding within spectrograph. -> distortion.

Answer is do lots of cals.

https://www.simplify3d.com/support/materials-guide/properties-table/

..
    % (iv (setq aperturecm (* 5.5 2.54 )))    13.97
    % (iv (setq theta (/ (* 1.22 5e-5) aperturecm) ))   4.366499642090193e-06
    % (iv (setq tmp (* theta 206264.8 )))   0.9006551753758051
    % (iv (setq tmp (/ (* 1.22 5e-5) (/ 1.0 206265.8 ) 2.54)))   4.95362748031496
    % (iv (setq tmp (/ (* 1.22 5e-5) (/ 1.0 206265.8 ))))   12.582213799999998

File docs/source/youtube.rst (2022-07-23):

YouTube Resources
=================

A work about YouTube: Many tutorials are made my 
non-American producers are are excellent in content.
Lately, many are just music with no words. Be patient
and shop around. 

YouTube resources. Google the title, and you should
find a quick URL to the resource. Combine with terms
like Learning Resources, Tutorials, Examples, and
phrases related to your specific question. For
example "SolidWorks equation driven parabola"

3D Printing 
-----------

    - 3D Printing Nerd
    - CHEP Filament Friday
    - Technivorous
    - Thomas Sanladerer
    - Prusa 3D by Josef Prusa
    - Tech2C
    - Zack Freedman
    - Core Electronics 3D Printing
    - DIY BuilderDIY Builder

Arduino 
-------

    - Adafruit Industries
    - Andreas Spiess
    - Core Electronics
    - Digi-Key
    - DIY Builder
    - Electronoobs
    - MERT Arduino & Tech
    - Seeed Studio
    - Alexander Baran-Harper

CAD/CAE 
-------

   - Hawk Ridge SolidWorks

Computer Hardware 
-----------------

    - Explaining Computers
    - Dronebot Workshop
    - The 8-Bit Guy
    - Ben Eater
    - Digi-Key

Computer Languages YouTube
--------------------------

    - Tech with Tim
    - Traversy Media
    - Adafruit Industries
    - Ben Eater
    - Caleb Curry
    - Core Electronics
    - TechGumbo
    - Alexander Baran-Harper

DIY 
---

    - Jake’s Workshop
    - Make it Extreme
    - MickMake
    - Ralph S Bacon
    - Zack Freedman
    - Andreas Spiess
    - Core Electronics
    - DIY Builder
    - Electronoobs
    - GreatScott!!
    - learnelectronics
    - MERT Arduino & Tech
    - The Thought Emporium

Electronics YouTube
-------------------

    - Dronebot Workshop
    - Kevin Darrah
    - Ralph S Bacon
    - Adafruit Industries
    - Andreas Spiess
    - Core Electronics
    - Ben Eater
    - Crosstalk Solutions
    - Digi-Key
    - DIY Builder
    - Electronoobs
    - GreatScott!!
    - learnelectronics
    - MERT Arduino & Tech
    - Seeed Studio
    - Alexander Baran-Harper
    - TheRaspberryPiGuy

Math 
----

    - 3Blue1Brown
    - Corey Schafer
    - patrickJMT

Networking YouTube
------------------

    - CWNE88
    - Crosstalk Solutions

Physics
-------

    - patrickJMT

Raspberry Pi YouTube
--------------------

    - Ralph S Bacon
    - Explaining Computers
    - Dronebot Workshop
    - Adafruit Industries
    - Andreas Spiess
    - Core Electronics
    - Crosstalk Solutions
    - Digi-Key
    - learnelectronics
    - Seeed Studio
    - Alexander Baran-Harper
    - TheRaspberryPiGuy

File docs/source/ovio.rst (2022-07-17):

OVIO Slit
=========

The OVIO slit is a chrome-plated 1.5mm glass substrate and has 12
positions/widths:

.. list-table:: Ovio Slit
   :widths: 10 50
   :header-rows: 1

   * - Position
     - Size
   * - 1
     - 10 microns
   * - 2
     - 20 microns
   * - 3
     - 30 microns
   * - 4
     - 40 microns
   * - 5
     - 50 microns
   * - 6
     - 70 microns
   * - 7
     - 100 microns
   * - 8
     - 150 microns
   * - 9
     - 200 microns
   * - 10
     - 300 microns
   * - 11
     - 500 (Shutter)
   * - 12
     - 700 microns

The 500 micron (next to largest size) is blocked to be used as a
simple shutter to allow taking zero and dark imagess during the
daytime.

The slit disc thickness is 1.5 mm.

The slit length is 6mm which is larger than most commercial
spectrographs. Benefits are easier placement of targets in the
guide camera field of view and greater coverage of extended
objects.

We are testing the orientation of the slit with respect to the sky.
Shiny toward the grating produces a caustic

We briefly investigated the idea of reversing the slit in its
holder such that the mirrored side faces the incoming beam.
We found that the guide image was noticeably improved in
briightness and that secondary images associated with bright
stars were removed. 

We did not detect any degradation in the recorded spectra,
however, we have maintained the convestion of a "reversed" OVIO
wheel for the present until we can investigate further.

The following images show a white light bench test of both
orientations.

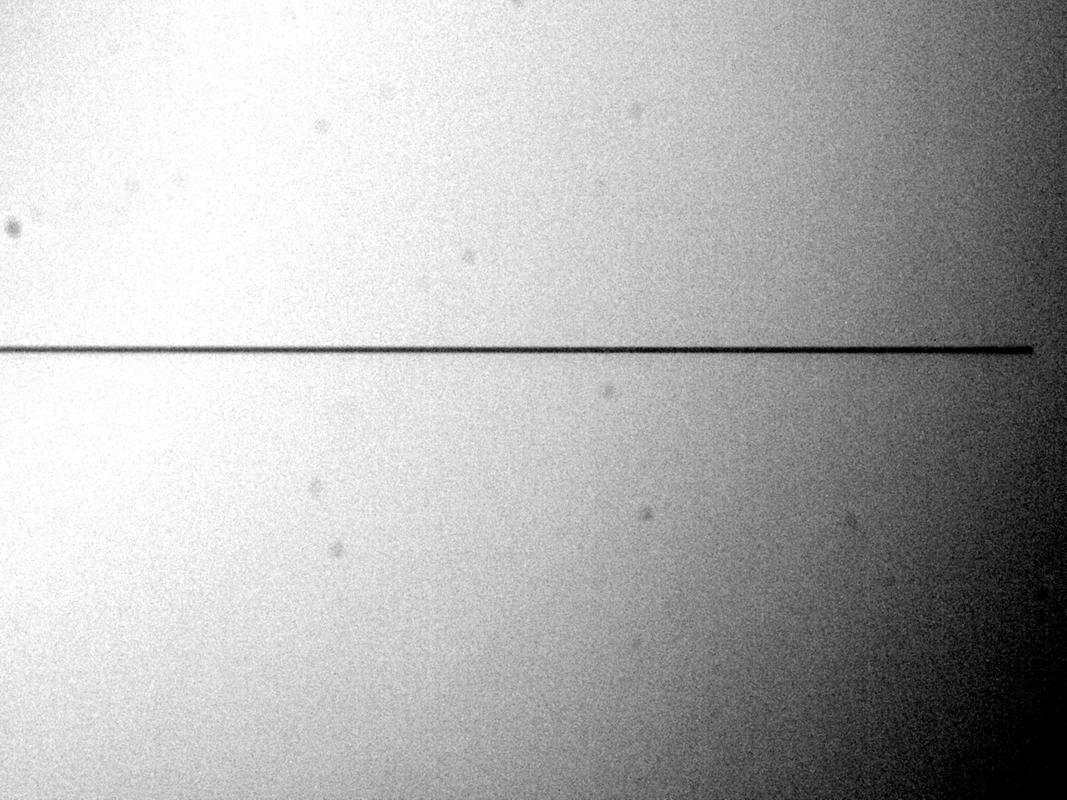
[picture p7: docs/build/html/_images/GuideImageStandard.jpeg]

  
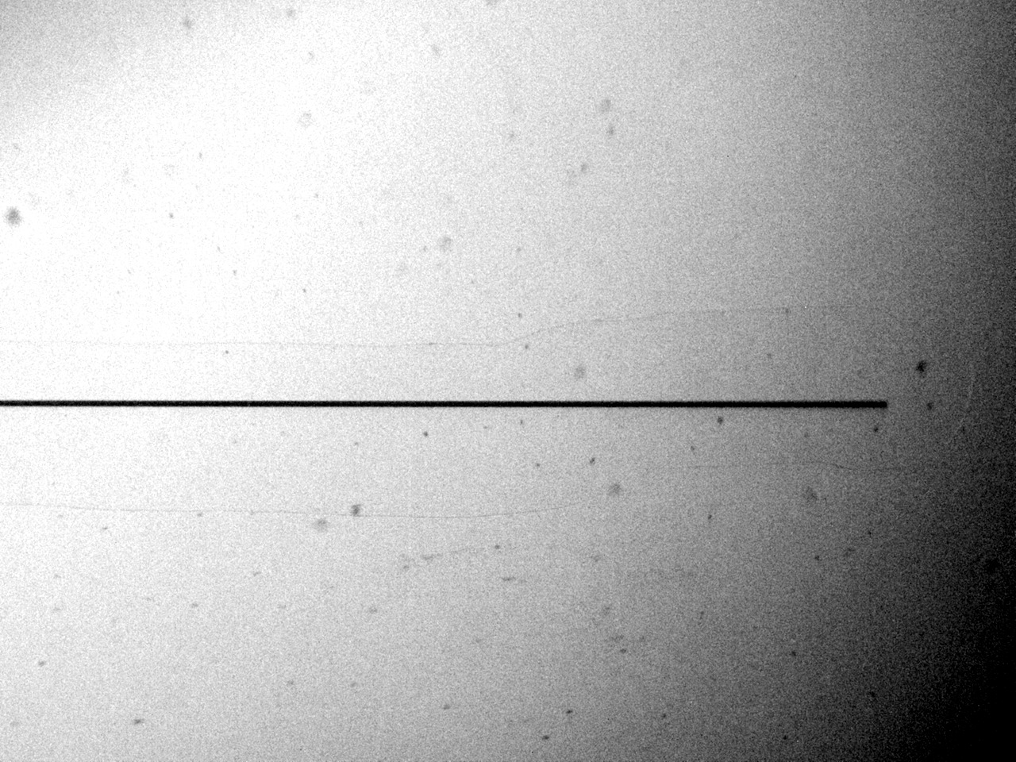
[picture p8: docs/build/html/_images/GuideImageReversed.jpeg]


We also investigated the Fraunhofer diffraction pattern as it
emerges from the spectrograph side of the slit because theory
predicts that this will cause a degradation in overall spectra
SNR due to stray light patterns withion the spectrograph body.

INSERT IMAGE - Waynes diffraction pattern.

This is shown in the attached image which is a highly
magnified view of the slit taken from the science camera
with the grating replaced by a mirror in the zeroeth order.
 
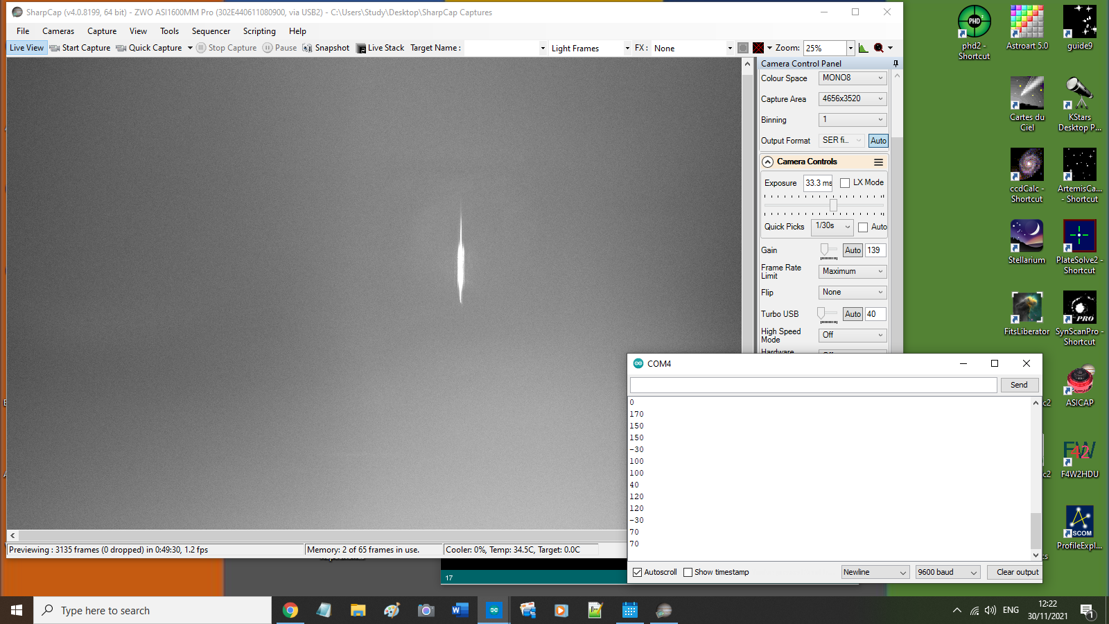
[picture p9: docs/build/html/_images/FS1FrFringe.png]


The fringe pattern can clearly be seen. Approximately 
95% of the signal is contained within the first lobe.
Additional lobes will cause noise in the signal through
loss of collimation and focus.

We remedied this by inserting a baffle behind the OVIO
mounting such that the width of the baffle exit pupil 
removed the unwanted lobes.  This appreciably improved 
the sharpness of the spectral calibration lines.

Since this effect is clearly dependent upon wavelength
and the focal ratio of the incoming beam a compromise 
baffel exit pupil width must be allowed to accomodate
both the red and blue ends of the spectrum.

In addition, a baffle must be made for each desired 
telescope focal ratio.  The baffles are easy to modify
and fit as a 3D printed part.
 
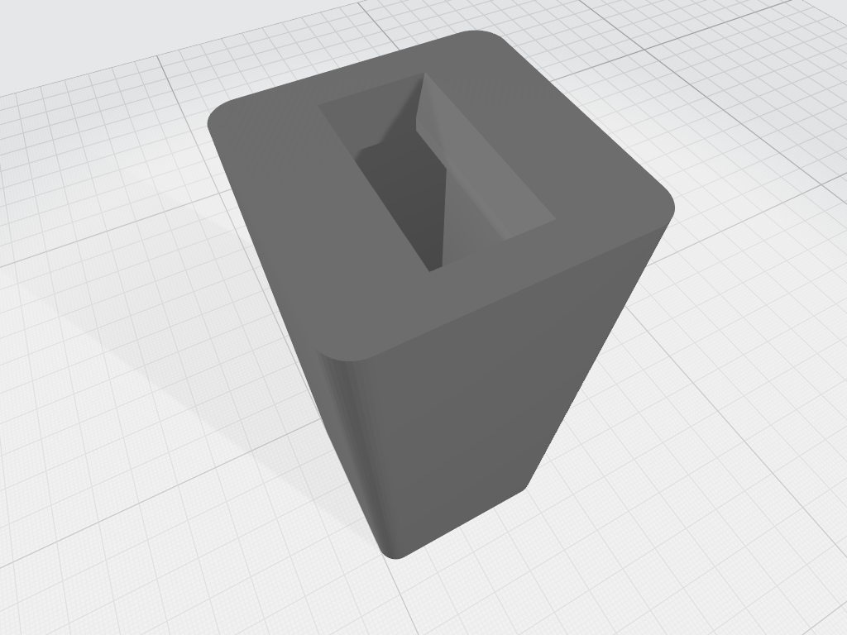
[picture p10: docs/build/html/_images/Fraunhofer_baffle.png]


The position of the baffle is shown in the following 
figure.  It can be seen as the red protrusion 
attached to the rear of the OVIO wheel mount.
 


A development for the FS2 will be a motorised selectable
slit wheel.

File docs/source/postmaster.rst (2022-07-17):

Postmaster
==========

There are a few paradigms of FlexSpec1.

#. A "Postmaster"/"Patron"/"Parcel" paradigm. The Bokeh server sends
   its information to the RPi PostmasterServer that acts as a
   'dispatch-server'. It adds keys to 'wrapper' a few things in a
   "Parcel" that is sent to the 'Serial' device requested by
   Bokeh. This parcel is unwrapped and routines are dispatched to C++
   classes within the Arduino.

#. The "matched class" paradigm -- a python class maintains variables related to a
   widget, that are encapsulated within a json string and sent to the Arduino (other)
   for processing. It contains the name of the device, the name of the widget in the
   device and a set of key/value pairs to be mirrored and acted upon by the "matched"
   C++ class in the Arduino.

#. JSON is used in a pure ASCII form. Numbers are strings, that are converted by
   the C++ mechanism within the Arduino. This avoids any Big/Little Endian issues
   and allows a simple terminal for monitoring the exchanges.

#. Error handling means a) someone cares, b) something meaningful may be done, and
   c) the error may be communicated. To get around this, add error checking is
   done by Bokeh at that end -- and we ASSUME, you know what that means, all
   input is legal.

The form is::

    { "DeviceName" : 
       { "Target C++  Widget" : 
          { "Process" : {"key" : "value", ... , "key" : "value" }}
          { "Report" : "1" }
       }
    }

Here The receiving serial port checks that it is within a device "DeviceName".
The "Target C++  Widget" is mapped to a Patron pointer. If the name is invalid,
the map returns a null and the packed is silently dropped. The dispatcher
validates the "command" (Process in this example) is a valid virtual member
of the Patron class - and that "value" which is a simple JSON string of
key/values for the member variables for that class are accepted and acted
upon.

For example for an IMU, the request might read "IMU" : {"x" : "1", "y" : "1", "z" : "1"}.
The dispatcher verifies that IMU exists, the Process() function reads the port,
sets internal variables. A second "Report" ... is requested, and the process
unwinds to send a message back to the Bokeh class making the request. 

Returning values update the Bokeh widget. In the case of the "Grating", the
wavelength may not be precise, as the motor has finite steps that may not
fall exactly where requested. The "Grating" class computes the CWAVE it
can achieve, reports back; the Bohek class updates the browser with the achieved
value.

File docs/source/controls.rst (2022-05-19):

.. _fs1-ecosystem:

FlexSpec 1 Ecosystem
********************

Use Case: Develop a basic GUI to Arduino Test case that will be the 
basis for all Arduinos.

..   figure:: ./images/PiggyBackBllinky.png

     PiggyBack is the name of an Arduino, on an OTA, "piggybacked" onto
     the main spectrgraph OTA. The On/Off radio buttons originate
     a message down to the device. It advertises text in a SandStone
     coloured box, and allows a integer value to be entered for the
     Pause Rate and Cycle Count for the Blinky Object Chain.

Control Overview
----------------

The FlexSpec 1 is designed to live with other devices under the umbrella
of a main scheduler. This requires partitioning each subsystem, and its
components in a way that information can be shared at within the instrument,
between other instruments, shared resources at a site and between other
layers within a master scheduler. The architecture of FlexSpec 1 is open.

..  figure:: ./images/FlexSpec_Comm_Regional.png

    Seen from the point-of-view of the Main OTA: The Raspberry PI has three means of communication: Ethernet with the world; Serial (1.8V/Voltage management) with Arduino SBMs; I2C for short haul with SMBs and stand alone sensors. Each sub-system is managed by its own collection of C++/Python classes.

The best way to approach the control structure is to start at the distal
end of the control message chain -- the actual component being controlled.

The component is implemented using a C++ class within the arduino. There
may be a few implementations of these classes -- depending on the 
architectural type of the Arduino/other device used. C++ classes
are used, as several of the same component may appear in one FlexSpec 1
instrument. They are disambiguated using a name.

Classes consist of "data+methods". The data is always present when
included in a compiled program. However the data portion is only
created when a class is instantiated.

..  figure:: ./images/GUI_Hardware.png

    The Ethernet provides a potential connection to the world. The Browser in the world serves a HTML DIV for each of the instantiated devices, shown here with a darker green background. Here we have a power block "Blinky Power" -- with lots of switches; A LowRez configuration spectrograph with its slit positioner, its grating selector and a Calibration Lamp for NeAr.

In the figure, each "instantiated device". In the case of the Slit
Positioner "Slit LoRez" a motor, that is permitted to make full
rotations. It is controlled by an instance of a C++ class running
within its controlling Arduino. It is physically wired and resides on
a multi-drop line. The "shim" that connects this physical device to
the outside world is an instance of a Bokeh class that translates the
HTML/JSNode events from the Browser into JSON strings to be shipped to
its associated widget within one of the arduinos attached to this
system. This is a common widely used protocol -- borrowed mostly from
the Data Visualization Community. It is extremely platform independent.

You can control your system with any enabled browser, on any device,
anywhere you are allowed to go: including NASA's Deep Space Network.

a C++ class instance running on an arduino connected by a "RS-232" type interface to its controlling Arduino residing on a multi-drop 

Scenario: Consider temperature sensors.

..  code-block:: none

    The generic temperature sensor: FlexTemperature
    Data: string Name
    Methods:
      FlexTemperature() // constructor
      FlexTemperature(const string &ref)
      void status(Message<x,y> &response)
      static FlexTemperature *factory(const string &ref)
    
In general a non-initialized constructor is only supported for
development. It costs nothing in terms of the code.

The construction with initialization capability of the form
FlexTemperature(const string &ref). The string is a narrow
subset of a JSON structure. The syntax is described 

This spectrograph uses several small single board computers with a serial
protocol to control:

- Slit selection

- Grating selection

- Focus of the colliminating lens

- Enabling one or more calibration lamps

  - High voltage lamps require a duty cycle

 -  High intensity (boosting blue) requires short cycle times

  - Colour LEDs to support gross grating position

- A slit back-illumination lamp

- Sensors for temperature and other aspects

- Orientation for parallactic angle measurement

The control elements essentially boil down to:
 
- Motor

- Sensor

- Switch

.. _fs1-control:

Control System
--------------
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

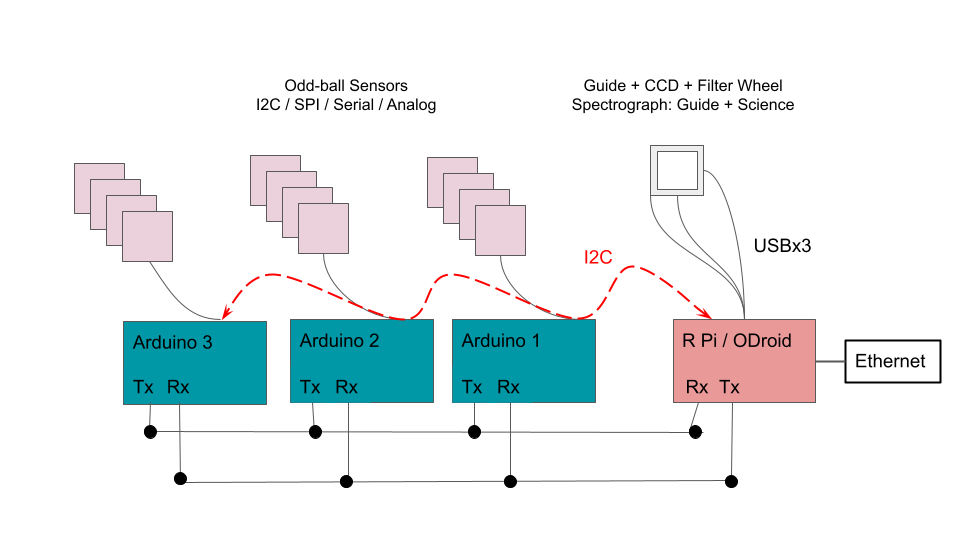
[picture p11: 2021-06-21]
docs/build/html/_images/FlexSpec_Comm_Regional.png

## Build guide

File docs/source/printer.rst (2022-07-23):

Printer
=======

3D Printer Calibration
Jerry Foote Oct 21, 2021

This procedure assumes that OctoPrint is attached and running. To send commands select
“Terminal” at the top of the screen and use the “Send” button to send the command to the
printer.

#. Send M503 command. Look for the M92 line and and note Current values for X, Y, Z and E.

#. Using printer controls heat up extruder temp to 190C for PLA or 245C for PETG.

#. Mark length of filament at 100mm & 120mm from the filament guide.

#. When hot, send command: G1 E100 F100

#. After the filament is extruded measure how much was extruded. If less than 100mm note how much, if more than 100, use 120 mark and compute how much. This is “ActualE”.

#. From the M92 command get the value for “E”= CurrentE.

#. Compute the new value for “E”, NewE= (100/ActualE)* CurrentE

#. Send M92 ENewE

#. Print 20 cm cube. https://www.thingiverse.com/thing:1278865

#. Measure X, Y, Z dimensions (X is right to left, Y is front to back and Z is verticle)

#. Compute New X = (20/ActualX) * CurrentX

#. Compute New Y = (20/ActualY) * CurrentY

#. Compute New Z = (20/ActualZ) * CurrentZ

#. Send M92 XNewX YNewY ZNewZ This command should format like the M92 command previously but with the new values.

#. Send M500 which saves these values.

#. Repeat process and fine tune values.

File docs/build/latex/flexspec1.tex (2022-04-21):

%% Generated by Sphinx.
\def\sphinxdocclass{report}
\documentclass[letterpaper,10pt,english,openany,oneside]{sphinxmanual}
\ifdefined\pdfpxdimen
   \let\sphinxpxdimen\pdfpxdimen\else\newdimen\sphinxpxdimen
\fi \sphinxpxdimen=.75bp\relax

\PassOptionsToPackage{warn}{textcomp}
\usepackage[utf8]{inputenc}
\ifdefined\DeclareUnicodeCharacter
% support both utf8 and utf8x syntaxes
  \ifdefined\DeclareUnicodeCharacterAsOptional
    \def\sphinxDUC#1{\DeclareUnicodeCharacter{"#1}}
  \else
    \let\sphinxDUC\DeclareUnicodeCharacter
  \fi
  \sphinxDUC{00A0}{\nobreakspace}
  \sphinxDUC{2500}{\sphinxunichar{2500}}
  \sphinxDUC{2502}{\sphinxunichar{2502}}
  \sphinxDUC{2514}{\sphinxunichar{2514}}
  \sphinxDUC{251C}{\sphinxunichar{251C}}
  \sphinxDUC{2572}{\textbackslash}
\fi
\usepackage{cmap}
\usepackage[T1]{fontenc}
\usepackage{amsmath,amssymb,amstext}
\usepackage{babel}

\usepackage{times}
\expandafter\ifx\csname T@LGR\endcsname\relax
\else
% LGR was declared as font encoding
  \substitutefont{LGR}{\rmdefault}{cmr}
  \substitutefont{LGR}{\sfdefault}{cmss}
  \substitutefont{LGR}{\ttdefault}{cmtt}
\fi
\expandafter\ifx\csname T@X2\endcsname\relax
  \expandafter\ifx\csname T@T2A\endcsname\relax
  \else
  % T2A was declared as font encoding
    \substitutefont{T2A}{\rmdefault}{cmr}
    \substitutefont{T2A}{\sfdefault}{cmss}
    \substitutefont{T2A}{\ttdefault}{cmtt}
  \fi
\else
% X2 was declared as font encoding
  \substitutefont{X2}{\rmdefault}{cmr}
  \substitutefont{X2}{\sfdefault}{cmss}
  \substitutefont{X2}{\ttdefault}{cmtt}
\fi

\usepackage[Bjarne]{fncychap}
\usepackage{sphinx}

\fvset{fontsize=\small}
\usepackage{geometry}

% Include hyperref last.
\usepackage{hyperref}
% Fix anchor placement for figures with captions.
\usepackage{hypcap}% it must be loaded after hyperref.
% Set up styles of URL: it should be placed after hyperref.
\urlstyle{same}

\addto\captionsenglish{\renewcommand{\contentsname}{Contents:}}

\usepackage{sphinxmessages}
\setcounter{tocdepth}{2}

\title{FlexSpec 1}
\date{Apr 21, 2022}
\release{0.1}
\author{Jerrold L. Foote\and Wayne Green\and Greg Jones\and Frank Parks\and Anthony Rodda\and Forrest Sims\and Thomas C. Smith\and Clarke Yeager}
\newcommand{\sphinxlogo}{\vbox{}}
\renewcommand{\releasename}{Release}
\makeindex
\begin{document}

\pagestyle{empty}
\sphinxmaketitle
\pagestyle{plain}
\sphinxtableofcontents
\pagestyle{normal}
\phantomsection\label{\detokenize{index::doc}}

\begin{figure}[htbp]
\centering
\capstart

\noindent\sphinxincludegraphics{{FS1_Assembly_with_Baffle}.jpeg}
\caption{CAD Layout for optical components of the FlexSpec 1.}\label{\detokenize{index:id1}}\end{figure}

\sphinxAtStartPar
Ramifications of 3D printing leading to FlexSpec 1 (FS1):
Introducing the Flexible Spectrograph I
Small Telescope Spectrograph.

\sphinxAtStartPar
This is documentation, the project and our aspirations for developing
a science data quality 3D spectrograph that is ‘Flexible’.

\sphinxAtStartPar
It is a continuous in progress. Bear with us. Better yet, collaborate with us.

\chapter{ABSTRACT}
\label{\detokenize{abstract:abstract}}\label{\detokenize{abstract::doc}}
\sphinxAtStartPar
\sphinxstylestrong{Title}:  Lessons Learned from the FlexSpec1 Spectrograph

\sphinxAtStartPar
(Accepted TBD, Proceedings of the Small Telescope Symposium 2022, Society
for Astronomical Sciences).
\begin{description}
\item[{Authors}] \leavevmode{[}Jerrold L. Foote, Wayne Green, Greg Jones, Frank Parks, Anthony{]}
\sphinxAtStartPar
Rodda, Forrest Sims, Thomas C. Smith, Clarke Yeager

\end{description}

\sphinxAtStartPar
\sphinxstylestrong{Abstract}:
This final paper of the FlexSpec1 series presents lessons learned and applied to 3D\sphinxhyphen{}Printed/Hybrid spectrographs for small telescope science. We present a detailed analysis of the photon\sphinxhyphen{}path from source to sensor and the steps within the spectrograph to mitigate instrumentation issues.  We present the caliberation unit, the “Kzin” ring, as a stand\sphinxhyphen{}alone aspect of the project suited to all spectrographs. A full implementation is in the puiblic domain via Github. Public documentation is available via ReadTheDocs.io. The full design is available via GitHub, the documentation is at ‘readthedocs.io flexspec1 \textless{}\sphinxurl{https://flexspec1.readthedocs.io/en/latest}\textgreater{}\_.

\sphinxAtStartPar
\sphinxstylestrong{Note to Editor}:

\sphinxAtStartPar
The GitHub and readthedocs.io contents are currently being maintained
at the ‘private’ level until release.

\chapter{Download FlexSpec1 Files}
\label{\detokenize{flexspec1:download-flexspec1-files}}\label{\detokenize{flexspec1::doc}}
\sphinxAtStartPar
FlexSpec1 is managed and distributed using the super zip\sphinxhyphen{}like
*cough* environment managed by the free \sphinxstylestrong{git} source code management (SCM)
system. Git will manage anything, not just computer code. So, we use
it! We distribute the STL files, and their original package’s
sources. SLDPRT for Solidworks for example. We also distribute code
for the Raspberry Pi, Arduinos, documentation, python utilities.  We
greatly appreciate SolidWorks support of community education projects.
We use KiCAD (pronounced “Kee CAD”) for EDA (Electronic Design
Automation) schematics. We may use other CAD programs to make
files. FreeCad is the latest adventure. Our general rule is to use
free or accessible software so everyone may participate. This means
any age, anywhere, anytime.

\sphinxAtStartPar
We are sharing a working dynamic release of the files and
documentation we develop for ourselves. Our files are your files. We
use the MIT license. This license boils down to copy\sphinxhyphen{}center. Take our
stuff to the copy\sphinxhyphen{}center and make all the copies you want. You can not
claim our work or limit our ownership. We can offer to share with you
and we do so freely. See the license for the liability statements etc.

\sphinxAtStartPar
\sphinxstylestrong{OK I want to build a spectrograph.}

\begin{sphinxVerbatim}[commandchars=\\\{\}]
\PYG{c+c1}{\PYGZsh{} Use PowerShell for Windows:}
mkdir C:\PYG{l+s+se}{\PYGZbs{}g}it
\PYG{n+nb}{cd} C:\PYG{l+s+se}{\PYGZbs{}g}it
git clone https://github.com/dxwayne/FlexSpec1
\end{sphinxVerbatim}

\sphinxAtStartPar
Or with \sphinxstylestrong{linux}:

\begin{sphinxVerbatim}[commandchars=\\\{\}]
\PYG{c+c1}{\PYGZsh{} Use bash for Mac/Linux}
mkdir \PYG{n+nv}{\PYGZdl{}HOME}/git
\PYG{n+nb}{cd} \PYG{n+nv}{\PYGZdl{}HOME}/git
git clone https://github.com/dxwayne/FlexSpec1
\end{sphinxVerbatim}

\sphinxAtStartPar
TaDa you have what we have.

\sphinxAtStartPar
\sphinxstylestrong{What did I get into?}

\sphinxAtStartPar
Under FlexSpec1/docs/source you find a bunch of .rst files. These
are used to make our \sphinxhref{https://flexspec1.readthedocs.io/en/latest/}{readthedocs.io files}
site. \sphinxstylestrong{Read All About It}.

\sphinxAtStartPar
In the lower\sphinxhyphen{}right of the page, you should find a little box:
“v:latest”. Hit that little down\sphinxhyphen{}caret and you can get a PDF.

\sphinxAtStartPar
This documentation is made with Sphinx documentation management, coordinated
with shared credentials with readthedocs.io.

\chapter{Open Questions}
\label{\detokenize{openquestions:open-questions}}\label{\detokenize{openquestions::doc}}
\sphinxAtStartPar
This is a very fluid section. Open questions are addressed here.

\sphinxAtStartPar
9 June 2021 Tony Rodda reported the fact that shifting the focus of
a commercial (Pentax) lens between he optical infinity mark and the
little ‘dot’ representing the infinity focus for infrared, the focus
changed over the dispersion axis.

\sphinxAtStartPar
\sphinxstylestrong{First and foremost:} we already know using a parabolic mirror as
a collimating lens is the best approach. The camera lens is
an expedient way to form the image.

\sphinxAtStartPar
This traces back to the fact that an achromat is balanced for two
of the Fraunhofer bands. An Apochromat is balanced for three. Lens
are basically prisms and focus is a function of wavelength.

\sphinxAtStartPar
\sphinxstylestrong{We determined}: The normal for the camera lens has to be tilted
a very small amount to compensate for spectral focus shift across
the dispersion axis projected onto the sensor.

\sphinxAtStartPar
\sphinxstylestrong{We note}: most inexpensive cameras do not maintain enough simple
quality control to make the sensor normal to the optical axis. Since
after\sphinxhyphen{}market measures are needed to compensate for the tilt, might
as well “feature it”. The difference between a “Bug” and a “Feature”
is the necktie!

\begin{figure}[htbp]
\centering

\noindent\sphinxincludegraphics{{BugFeature}.png}
\end{figure}

\sphinxAtStartPar
The use of a commercial camera lens also helps in achieving a
flatter field for the science camera (which then improves
calibration) and assists greatly with maintaining overall
collimation.

\chapter{OVIO Slit}
\label{\detokenize{ovio:ovio-slit}}\label{\detokenize{ovio::doc}}
\sphinxAtStartPar
The OVIO slit is a chrome\sphinxhyphen{}plated 1.5mm glass substrate and has 12
positions/widths:

\begin{savenotes}\sphinxattablestart
\centering
\sphinxcapstartof{table}
\sphinxthecaptionisattop
\sphinxcaption{Ovio Slit}\label{\detokenize{ovio:id1}}
\sphinxaftertopcaption
\begin{tabular}[t]{|\X{10}{60}|\X{50}{60}|}
\hline
\sphinxstyletheadfamily 
\sphinxAtStartPar
Position
&\sphinxstyletheadfamily 
\sphinxAtStartPar
Size
\\
\hline
\sphinxAtStartPar
1
&
\sphinxAtStartPar
10 microns
\\
\hline
\sphinxAtStartPar
2
&
\sphinxAtStartPar
20 microns
\\
\hline
\sphinxAtStartPar
3
&
\sphinxAtStartPar
30 microns
\\
\hline
\sphinxAtStartPar
4
&
\sphinxAtStartPar
40 microns
\\
\hline
\sphinxAtStartPar
5
&
\sphinxAtStartPar
50 microns
\\
\hline
\sphinxAtStartPar
6
&
\sphinxAtStartPar
70 microns
\\
\hline
\sphinxAtStartPar
7
&
\sphinxAtStartPar
100 microns
\\
\hline
\sphinxAtStartPar
8
&
\sphinxAtStartPar
150 microns
\\
\hline
\sphinxAtStartPar
9
&
\sphinxAtStartPar
200 microns
\\
\hline
\sphinxAtStartPar
10
&
\sphinxAtStartPar
300 microns
\\
\hline
\sphinxAtStartPar
11
&
\sphinxAtStartPar
500 (Shutter)
\\
\hline
\sphinxAtStartPar
12
&
\sphinxAtStartPar
700 microns
\\
\hline
\end{tabular}
\par
\sphinxattableend\end{savenotes}

\sphinxAtStartPar
The 500 micron (next to largest size) is blocked to be used as a
simple shutter to allow taking zero and dark imagess during the
daytime.

\sphinxAtStartPar
The slit disc thickness is 1.5 mm.

\sphinxAtStartPar
The slit length is 6mm which is larger than most commercial
spectrographs. Benefits are easier placement of targets in the
guide camera field of view and greater coverage of extended
objects.

\sphinxAtStartPar
We briefly investigated the idea of reversing the slit in its
holder such that the mirrored side faces the incoming beam.
We found that the guide image was noticeably improved in
briightness and that secondary images associated with bright
stars were removed.

\sphinxAtStartPar
We did not detect any degradation in the recorded spectra,
however, we have maintained the convestion of a “reversed” OVIO
wheel for the present until we can investigate further.

\sphinxAtStartPar
The following images show a white light bench test of both
orientations.

\begin{figure}[htbp]
\centering

\noindent\sphinxincludegraphics{{GuideImageStandard}.jpeg}
\end{figure}

\begin{figure}[htbp]
\centering

\noindent\sphinxincludegraphics{{GuideImageReversed}.jpeg}
\end{figure}

\sphinxAtStartPar
We also investigated the Fraunhofer diffraction pattern as it
emerges from the spectrograph side of the slit because theory
predicts that this will cause a degradation in overall spectra
SNR due to stray light patterns withion the spectrograph body.

\sphinxAtStartPar
INSERT IMAGE \sphinxhyphen{} Waynes diffraction pattern.

\sphinxAtStartPar
This is shown in the attached image which is a highly
magnified view of the slit taken from the science camera
with the grating replaced by a mirror in the zeroeth order.

\begin{figure}[htbp]
\centering

\noindent\sphinxincludegraphics{{FS1FrFringe}.png}
\end{figure}

\sphinxAtStartPar
The fringe pattern can clearly be seen. Approximately
95\% of the signal is contained within the first lobe.
Additional lobes will cause noise in the signal through
loss of collimation and focus.

\sphinxAtStartPar
We remedied this by inserting a baffle behind the OVIO
mounting such that the width of the baffle exit pupil
removed the unwanted lobes.  This appreciably improved
the sharpness of the spectral calibration lines.

\sphinxAtStartPar
Since this effect is clearly dependent upon wavelength
and the focal ratio of the incoming beam a compromise
baffel exit pupil width must be allowed to accomodate
both the red and blue ends of the spectrum.

\sphinxAtStartPar
In addition, a baffle must be made for each desired
telescope focal ratio.  The baffles are easy to modify
and fit as a 3D printed part.

\begin{figure}[htbp]
\centering

\noindent\sphinxincludegraphics{{Fraunhofer_baffle}.png}
\end{figure}

\sphinxAtStartPar
The position of the baffle is shown in the following
figure.  It can be seen as the red protrusion
attached to the rear of the OVIO wheel mount.

\begin{figure}[htbp]
\centering

\noindent\sphinxincludegraphics{{FS1_Assembly_with_Baffle}.jpeg}
\end{figure}

\sphinxAtStartPar
A development for the FS2 will be a motorised selectable
slit wheel.

\chapter{Care of Optics}
\label{\detokenize{optics:care-of-optics}}\label{\detokenize{optics::doc}}
\sphinxAtStartPar
When handling optics uses gloves, nitrile or pure clean untreated
cotton gloves. This will protect the optical elements and protect
you from harsh cleaning chemicals. Optics should be stored in an
airtight container to avoid reaction with pollutants.
\begin{enumerate}
\sphinxsetlistlabels{\arabic}{enumi}{enumii}{}{.}%
\item {} 
\sphinxAtStartPar
\sphinxstylestrong{Never} use silcone based adhesives or silicone based lubricants any
where near optics. They outgas and condense on the optical surfaces.

\item {} 
\sphinxAtStartPar
The optics should never be touched with your bare hands.  Always
use clean powder free latex or nitrile gloves. Finger prints leave
oils, acids and other volatiles on the surfaces which in the cases of
gratings can not be removed. On lenses or mirrors they may etch the
surface coatings.

\item {} 
\sphinxAtStartPar
If after careful handling a finger print gets on the surface a
micro fiber cloth may remove it if used gently.  DON’T try to wipe a
grating it will scratch.

\item {} 
\sphinxAtStartPar
Front surface mirrors are also fragile. Usually they are over
coated for protection but the coating may be very thin.

\item {} 
\sphinxAtStartPar
Don’t use \sphinxstylestrong{Windex} ® to clean optics. It contains ammonia which
can remove aluminum coating. Use Everclear ® grain alcohol, 95\%
ethanol alcohol or commercial lens cleaning solution as a cleaning
fluid. Us it sparingly. Grain alcohol does not contain denaturing
agents and should not leave a fine white powder on optics.

\sphinxAtStartPar
Like most alcohols, isopropyl alcohol reacts with active metals
such as potassium to form alkoxides that can be called
isopropoxides. The reaction with aluminum (initiated by a trace
of mercury) is used to prepare the catalyst aluminum
isopropoxides. Most IPA isopropyl alcohol has denaturing
agents added and will leave a fine white powder.

\item {} 
\sphinxAtStartPar
Gratings are very susceptible to handling problems. Even with
gloves never touch the ruled surface.  Any scratches or finger prints
will introduce scattered light in to the system. A spectrograph is
always starved for light and to scatter some of the light will reduce
the throughput.

\end{enumerate}

\section{Tips for optics in a spectrograph}
\label{\detokenize{optics:tips-for-optics-in-a-spectrograph}}\begin{enumerate}
\sphinxsetlistlabels{\arabic}{enumi}{enumii}{}{.}%
\item {} 
\sphinxAtStartPar
Grating orientation: if a commercial blazed grating is used it
will have an arrow drawn on the top, bottom or both edges that are
perpendicular to the grooves.  This arrow shows the blaze
direction. The arrow should point toward the incoming beam.  This
orientation maximizes the energy into the first order. If the
arrow is missing it is possible to look into the spectrographs
camera port, without the camera lens in place, while light is
shinning on the slit, rotate the grating so that the zero’th order
can be seen. Then rotate the grating further to pick up the
spectrum starting with the blue end. Further grating rotation will
the bring up the second order. The first order should be very much
brighter than the second order.  If it isn’t the grating
orientation in the holder should be reversed.

\item {} 
\sphinxAtStartPar
If the dispersion along the image from the sensor is not
horizontal (follows a ‘row’ of pixels), the camera needs to be
rotated such that it is.

\item {} 
\sphinxAtStartPar
If the calibration lamp emission lines are not vertical with
respect to the grating; the OVIO slit needs to be rotated in it’s
holder to make them vertical. This can be fiddly sometimes to get
right. Also the vertical slit must be co\sphinxhyphen{}linear with the grating
grooves.

\item {} 
\sphinxAtStartPar
If lenses are not a snug fit into their holders a small
application of white glue on the holder will hold them in place
but allow later removal if needed. Don’t get a glue string on the
lens.

\item {} 
\sphinxAtStartPar
If the lens is a snug fit into the holder make sure that you don’t
apply too much pressure to insert it. Some lower quality achromat
lens elements are not glued in a way that is precisely centered
and while pushing it in an edge might get caught and split the
elements apart.

\item {} 
\sphinxAtStartPar
Depending on many factors (lens focal length, aperture, quality)
the blue and red ends of the spectra may be out of focus while the
center is sharp. This is normal with simple achromat lenses used
for the camera lens. If a commercial photographic lens is used for
the camera lens this is much less of a problem as the multiple
elements in the commercial lens are designed to flatten the field.

\item {} 
\sphinxAtStartPar
When combined with large chips, short focal length lenses, with
short radii may require the sensors plane to be shifted. This is
easily achieved with after\sphinxhyphen{}marked sensor/camera tilt correctors.

\item {} 
\sphinxAtStartPar
A Cheshire eyepiece (laser collimator) is a very handy tool to get
things lined up in the spectrograph, particularly the guide mirror
and main mirror. It is also an easy way to check if the grating is
mounted with it’s surface parallel with the rotation stage. If it
is a green laser and the grating stage rotated till the beam is
centered in the camera port, then the first spectra will be close
to centered. If red then adjust the grating angle such that it is
where H\sphinxhyphen{}alpha emission is expected on the image.

\item {} 
\sphinxAtStartPar
Achromat lens orientation. When mounting lenses the side with the
bigger “bulge” should be oriented toward the grating. Both for the
collimating lens as well as the camera lens.

\end{enumerate}

\chapter{Optical Experiments}
\label{\detokenize{experiments:optical-experiments}}\label{\detokenize{experiments::doc}}
\sphinxAtStartPar
There are several optical experiments to consider.
\begin{enumerate}
\sphinxsetlistlabels{\arabic}{enumi}{enumii}{}{.}%
\item {} 
\sphinxAtStartPar
Orientation of grating.

\item {} 
\sphinxAtStartPar
Focus of the camera/collimator.

\end{enumerate}

\section{Orientation of Grating}
\label{\detokenize{experiments:orientation-of-grating}}
\sphinxAtStartPar
Commercial spectrographs have been received with the grating
facing the wrong way. This is a simple experiment to determine
the direction of the blazed order:

\sphinxAtStartPar
Materials:
\begin{enumerate}
\sphinxsetlistlabels{\arabic}{enumi}{enumii}{}{.}%
\item {} 
\sphinxAtStartPar
A dimmer laser pointer.

\end{enumerate}

\sphinxAtStartPar
\#. A simple littrow prism from Surplus Shed. (L2003D) or a Herschel wedge
solar ‘filter’.
\begin{enumerate}
\sphinxsetlistlabels{\arabic}{enumi}{enumii}{}{.}%
\item {} 
\sphinxAtStartPar
White Index Card

\end{enumerate}

\sphinxAtStartPar
Open the spectrograph just enough to insert the card, and shine the laser beam
onto the grating. The angle is not that important for this test a large angle
will be OK \textendash{} as long as it is not too large.

\sphinxAtStartPar
The littrow prism/Herschel wedge reduces the laser brightness by about 95 percent.
If the laser pointer is very dim, it is not needed.

\sphinxAtStartPar
Place a white card to receive the reflection of a dim laser beam. The brightest
dot is the specular reflection (non\sphinxhyphen{}dispersed order\sphinxhyphen{}0 beam). The brightest
spot will be the ‘blazed’ beam. This is most often the +1 order. On rare
occasions (surplus gratings for example) may have the blaze set to a different
order.

\section{Focus of the Camera/Collimator}
\label{\detokenize{experiments:focus-of-the-camera-collimator}}
\sphinxAtStartPar
In order to achieve and maintain accurate collimation to and from
the grating we find that focusing the science camera on infinity at the
outset and solely focusing the collimationg mirror during operation
results in the best possible set up.  This may seem obvious but most
commercial spectrographs allow the user to change the science camera
focus during an observing session (because the collimating mirror is
usually inaccessible).  This may be necessary because of thermal
changes or flexure in the spectrograph body.  The result is
a badly collimated system.

\sphinxAtStartPar
We suggest the following method of set up.

\sphinxAtStartPar
Position a camera (a DSLR will work) with its lens focused for
infinity using a very distant point source. A far away
street\sphinxhyphen{}light or a bright star works. Most commercial camera
lenses will focus IR light, hence the full stop is NOT
focused for visible light.

\sphinxAtStartPar
Place a front surface mirror at the grating position, and the camera
at the exit ‘camera’ port of the spectrograph. Then focus the slit’s
image using the collimating mirror. This is a ‘real’ close
approximation for the collimator lens focus.

\sphinxAtStartPar
The FlexSpec has a remote collimating mirror adjuster driven by
a stepper motor and eccentri cam arrangement for fine focus during
an observing session.  This means the FlexSpec can be focused
without touching.

\sphinxAtStartPar
Future FlexSpec will have a remote\sphinxhyphen{}selectable grating changer. Plans
are to include a front\sphinxhyphen{}surface mirror.

\chapter{OVERVIEW}
\label{\detokenize{overview:overview}}\label{\detokenize{overview::doc}}
\sphinxAtStartPar
This documentation has all {\hyperref[\detokenize{bom:flexspec1-bom}]{\sphinxcrossref{\DUrole{std,std-ref}{bill\sphinxhyphen{}of\sphinxhyphen{}materials}}}} and in\sphinxhyphen{}depth discussion of
the concepts, development, technical and scientific aspects of
Flexspec 1. “Flexible” is “Flexible”. A concrete example
of the Flexspec 1 is presented but the ideas, CAD drawings,
software and documentation are available in the public\sphinxhyphen{}domain
for vendors and fellow small telescope scientists to use and
enjoy.

\sphinxAtStartPar
During an after\sphinxhyphen{}meeting in Flagstaff, AZ in late 2018 a few of the
authors met and developed the idea of leveraging Paul Gerlach’s
LOWSPEC 3D Printed spectrograph as a means of gaining more data from
the small telescope community. In early 2019, at the Sacramento
Mountains Spectroscopy Workshop II in Las Cruces NM the decision was
taken to refine 3D printed spectrographs. This collaboration will
continue beyond this paper.

\sphinxAtStartPar
The Flexspec 1 small instrument operating as a full peer within a
network of sites with other instruments.  Flexspec employs multiple
control components and can share its state\sphinxhyphen{}of\sphinxhyphen{}affairs with other
interested control elements throughout its associated networks. For
example, one does not start a deep spectral exposure while a neighbor
in a roll\sphinxhyphen{}off building is taking dome flats. We made an attempt to
design a control messaging architecture to address the full
control/scheduler issue. Those implementation details will be
addressed in future. See Section {\hyperref[\detokenize{controls:fs1-control}]{\sphinxcrossref{\DUrole{std,std-ref}{Controls}}}}.

\sphinxAtStartPar
Adding automated control elements such as motors, sensors, and
switches to a spectrograph were driven by experience and issues with
other instruments.

\sphinxAtStartPar
Issues include:
\begin{itemize}
\item {} 
\sphinxAtStartPar
\sphinxstylestrong{Thermal Expansion:} The complete thermal range is from daytime 118F to nighttime \sphinxhyphen{}20F depending on the season. 3D Plastics have high thermal expansion coefficients.

\item {} 
\sphinxAtStartPar
\sphinxstylestrong{Flexture:} PLA/Plastics are highly flexible. Threads are unreliable.

\item {} 
\sphinxAtStartPar
\sphinxstylestrong{Focus:} Temperature changes across a night, bench setup.

\item {} 
\sphinxAtStartPar
\sphinxstylestrong{Seeing:} Seeing conditions are variable as small telescope work is done deep in the atmosphere.

\item {} 
\sphinxAtStartPar
\sphinxstylestrong{Parallactic Angle:} Always a concern. The Arduino Nano Sense 33 IoT (BLE) provides rotator feedback.

\item {} 
\sphinxAtStartPar
\sphinxstylestrong{Remote use:} Here Office to backyard was the goal, architecture was global.

\end{itemize}

\sphinxAtStartPar
During 2020 we became aware of thermal and structural issues. Yeager
did the bulk of these experiments in the the cold Colorado winter.
This year’s work concentrated on the math, physics, optics, and
engineering aspects of the spectrograph. There have been requests for
accommodating apertures beyond the nominal 11\sphinxhyphen{}inch SCT telescopes, to
include short\sphinxhyphen{}focus (f/5 \sphinxhyphen{} f/8) instruments; and apertures in the
ranges of 36\sphinxhyphen{}60cm and beyond.

\index{issues@\spxentry{issues}!thermal@\spxentry{thermal}}\index{issues@\spxentry{issues}!flexure@\spxentry{flexure}}\ignorespaces 
\sphinxAtStartPar
Matching the slit size to focal length and seeing. TODO Move this table.
\begin{quote}

\begin{savenotes}\sphinxattablestart
\centering
\begin{tabular}[t]{|*{8}{\X{1}{8}|}}
\hline

\sphinxAtStartPar
Aperture
&
\sphinxAtStartPar
f/ratio
&
\sphinxAtStartPar
fl
&
\sphinxAtStartPar
Magic
&\sphinxstartmulticolumn{4}%
\begin{varwidth}[t]{\sphinxcolwidth{4}{8}}
\sphinxAtStartPar
Seeing (arcsec)
\par
\vskip-\baselineskip\vbox{\hbox{\strut}}\end{varwidth}%
\sphinxstopmulticolumn
\\
\hline
\sphinxAtStartPar
(inch)
&
\sphinxAtStartPar
(inch)
&\begin{enumerate}
\sphinxsetlistlabels{\roman}{enumi}{enumii}{(}{)}%
\setcounter{enumi}{1999}
\item {} 
\end{enumerate}
&
\sphinxAtStartPar
“/\(\mu{m}\)
&
\sphinxAtStartPar
1
&
\sphinxAtStartPar
2
&
\sphinxAtStartPar
3
&
\sphinxAtStartPar
4
\\
\hline
\sphinxAtStartPar
6
&
\sphinxAtStartPar
5
&
\sphinxAtStartPar
735
&
\sphinxAtStartPar
0.28063
&
\sphinxAtStartPar
3.56338
&
\sphinxAtStartPar
7.12676
&
\sphinxAtStartPar
10.69014
&
\sphinxAtStartPar
14.25352
\\
\hline
\sphinxAtStartPar
6
&
\sphinxAtStartPar
6.7
&
\sphinxAtStartPar
984.9
&
\sphinxAtStartPar
0.20943
&
\sphinxAtStartPar
4.77493
&
\sphinxAtStartPar
9.54986
&
\sphinxAtStartPar
14.32479
&
\sphinxAtStartPar
19.09972
\\
\hline
\sphinxAtStartPar
6
&
\sphinxAtStartPar
8
&
\sphinxAtStartPar
1176
&
\sphinxAtStartPar
0.17540
&
\sphinxAtStartPar
5.70141
&
\sphinxAtStartPar
11.40282
&
\sphinxAtStartPar
17.10423
&
\sphinxAtStartPar
22.80564
\\
\hline
\sphinxAtStartPar
8
&
\sphinxAtStartPar
5
&
\sphinxAtStartPar
980
&
\sphinxAtStartPar
0.21047
&
\sphinxAtStartPar
4.75117
&
\sphinxAtStartPar
9.50235
&
\sphinxAtStartPar
14.25352
&
\sphinxAtStartPar
19.00470
\\
\hline
\sphinxAtStartPar
8
&
\sphinxAtStartPar
6
&
\sphinxAtStartPar
1176
&
\sphinxAtStartPar
0.17540
&
\sphinxAtStartPar
5.70141
&
\sphinxAtStartPar
11.40282
&
\sphinxAtStartPar
17.10423
&
\sphinxAtStartPar
22.80564
\\
\hline
\sphinxAtStartPar
8
&
\sphinxAtStartPar
10
&
\sphinxAtStartPar
1960
&
\sphinxAtStartPar
0.10524
&
\sphinxAtStartPar
9.50235
&
\sphinxAtStartPar
19.00470
&
\sphinxAtStartPar
28.50705
&
\sphinxAtStartPar
38.00939
\\
\hline
\sphinxAtStartPar
11
&
\sphinxAtStartPar
5
&
\sphinxAtStartPar
1347.5
&
\sphinxAtStartPar
0.15307
&
\sphinxAtStartPar
6.53286
&
\sphinxAtStartPar
13.06573
&
\sphinxAtStartPar
19.59859
&
\sphinxAtStartPar
26.13146
\\
\hline
\sphinxAtStartPar
11
&
\sphinxAtStartPar
11
&
\sphinxAtStartPar
2964.5
&
\sphinxAtStartPar
0.06958
&
\sphinxAtStartPar
14.37230
&
\sphinxAtStartPar
28.74460
&
\sphinxAtStartPar
43.11691
&
\sphinxAtStartPar
57.48921
\\
\hline
\sphinxAtStartPar
12
&
\sphinxAtStartPar
4
&
\sphinxAtStartPar
1176
&
\sphinxAtStartPar
0.17540
&
\sphinxAtStartPar
5.70141
&
\sphinxAtStartPar
11.40282
&
\sphinxAtStartPar
17.10423
&
\sphinxAtStartPar
22.80564
\\
\hline
\sphinxAtStartPar
12
&
\sphinxAtStartPar
13.5
&
\sphinxAtStartPar
3969
&
\sphinxAtStartPar
0.05197
&
\sphinxAtStartPar
19.24226
&
\sphinxAtStartPar
38.48451
&
\sphinxAtStartPar
57.72677
&
\sphinxAtStartPar
76.96902
\\
\hline
\sphinxAtStartPar
14
&
\sphinxAtStartPar
6.7
&
\sphinxAtStartPar
2298.1
&
\sphinxAtStartPar
0.08975
&
\sphinxAtStartPar
11.14150
&
\sphinxAtStartPar
22.28301
&
\sphinxAtStartPar
33.42451
&
\sphinxAtStartPar
44.56601
\\
\hline
\sphinxAtStartPar
14
&
\sphinxAtStartPar
8
&
\sphinxAtStartPar
2744
&
\sphinxAtStartPar
0.07517
&
\sphinxAtStartPar
13.30329
&
\sphinxAtStartPar
26.60658
&
\sphinxAtStartPar
39.90986
&
\sphinxAtStartPar
53.21315
\\
\hline
\sphinxAtStartPar
16
&
\sphinxAtStartPar
4
&
\sphinxAtStartPar
1568
&
\sphinxAtStartPar
0.13155
&
\sphinxAtStartPar
7.60188
&
\sphinxAtStartPar
15.20376
&
\sphinxAtStartPar
22.80564
&
\sphinxAtStartPar
30.40752
\\
\hline
\sphinxAtStartPar
16
&
\sphinxAtStartPar
13.5
&
\sphinxAtStartPar
5292
&
\sphinxAtStartPar
0.03898
&
\sphinxAtStartPar
25.65634
&
\sphinxAtStartPar
51.31268
&
\sphinxAtStartPar
76.96902
&
\sphinxAtStartPar
102.62536
\\
\hline
\sphinxAtStartPar
24
&
\sphinxAtStartPar
4
&
\sphinxAtStartPar
2352
&
\sphinxAtStartPar
0.08770
&
\sphinxAtStartPar
11.40282
&
\sphinxAtStartPar
22.80564
&
\sphinxAtStartPar
34.20845
&
\sphinxAtStartPar
45.61127
\\
\hline
\sphinxAtStartPar
24
&
\sphinxAtStartPar
8
&
\sphinxAtStartPar
4704
&
\sphinxAtStartPar
0.04385
&
\sphinxAtStartPar
22.80564
&
\sphinxAtStartPar
45.61127
&
\sphinxAtStartPar
68.41691
&
\sphinxAtStartPar
91.22255
\\
\hline
\end{tabular}
\par
\sphinxattableend\end{savenotes}

\sphinxAtStartPar
Table of focal lengths matching slit widths with seeing.
\end{quote}

\index{seeing@\spxentry{seeing}!slit width@\spxentry{slit width}}\ignorespaces 

\chapter{Physics}
\label{\detokenize{physics:physics}}\label{\detokenize{physics::doc}}
\sphinxAtStartPar
This section contains the basic mathematical underpinnings used in our
analysis of the basic DIY spectroscope.

\sphinxAtStartPar
The optical \index{sign conventions@\spxentry{sign conventions}}sign conventions used here follow Schroeder’s (1987)
“Cartesian” approach. The plane for the optics (“lens/mirror surfaces”)
are in the XY plane, the optical axis follows the Z axis.  Along the Z
axis, rays pass from the negative (lesser) to right
(greater). Reflections reverse the sign. (I.e.: photons move in the
positive direction along the Z axis.)

\sphinxAtStartPar
There are at least 6 dispersion techniques to consider:
\begin{itemize}
\item {} \begin{enumerate}
\sphinxsetlistlabels{\arabic}{enumi}{enumii}{(}{)}%
\item {} 
\sphinxAtStartPar
Fresnel (nearfield),

\end{enumerate}

\item {} \begin{enumerate}
\sphinxsetlistlabels{\arabic}{enumi}{enumii}{(}{)}%
\item {} 
\sphinxAtStartPar
Fraunhofer (slit) diffraction,

\end{enumerate}

\item {} \begin{enumerate}
\sphinxsetlistlabels{\arabic}{enumi}{enumii}{(}{)}%
\setcounter{enumi}{1}
\item {} 
\sphinxAtStartPar
Reflection and transmission diffraction gratings,

\end{enumerate}

\item {} \begin{enumerate}
\sphinxsetlistlabels{\arabic}{enumi}{enumii}{(}{)}%
\setcounter{enumi}{1}
\item {} 
\sphinxAtStartPar
Prisms and a grism (combination prism/transmission grating).

\end{enumerate}

\end{itemize}

\sphinxAtStartPar
A lot of the mathematical manipulations used here are accessible via
the \sphinxhref{https://www.wolframalpha.com}{Wolfram Alpha web site} , freely accessible and with paid
subscriptions.

\section{BOTE Computation}
\label{\detokenize{physics:bote-computation}}
\sphinxAtStartPar
To assist with basic design and to develop intuition, “Back of The
Envelope” \index{BOTE@\spxentry{BOTE}}BOTE computation is in
order. Astronomers utilize the “Centimeter Gram Seconds” (CGS)
system. Here are a few guide pointers:
\begin{enumerate}
\sphinxsetlistlabels{\arabic}{enumi}{enumii}{}{.}%
\item {} \begin{description}
\item[{Use the same units, here centimeters;}] \leavevmode\begin{itemize}
\item {} 
\sphinxAtStartPar
\(5 \times 10^{-5}\) cm for green light. \(5 \times 10^{-5}\) cm for blue and \(6 \times 10^{-5}\) cm for red. We use 300 and 600 l/mm gratings and the math cancels!

\item {} 
\sphinxAtStartPar
Translate grating \(l/mm\; to\l\) \(l/cm\)

\end{itemize}

\end{description}

\item {} 
\sphinxAtStartPar
Remember sign conventions, and get the right equation.

\item {} 
\sphinxAtStartPar
Follow the general spectrograph equation chain. Slit/grating/sensor.

\end{enumerate}

\section{Light}
\label{\detokenize{physics:light}}
\sphinxAtStartPar
A wavelength is a cycle, its length is a function of the energy of the
associated photon. An image has a ‘wavefront’ and that wavefront has a
quality, expressed in fractions of a wavelength (variation of 1/10th
of a wavelength \(2\times\pi/10 = 0.328\) (360 degrees for a full
cycle) amounts to a shift of around 36 degrees! A lot of error. Using
a ‘folding’ mirror \index{mirror@\spxentry{mirror}!folding@\spxentry{folding}}mirror;folding adds error. This same
wavefront error seeps in with irregular coatings and lens surfaces.  It
creeps in with the parallelism agreement between the front and back of a
lens; with the co\sphinxhyphen{}alignment of lenses; and with the flatness of a
grating’s plane.

\section{The Behavior of Lenses}
\label{\detokenize{physics:the-behavior-of-lenses}}
\sphinxAtStartPar
In theory, lenses work well. In practice there is the issue of the
agreement between the curve at the front of the lens and that at the
back of the lens (a wedge or a prism\sphinxhyphen{}astigmatism effect). The distance
between a surface at the edge adds additional chances for
dispersion of the light as it passes through the lens. The cheaper the
lens the more likely the lens has issues.

\sphinxAtStartPar
Glass refracts, deferentially, as a function of energy (wavelength).

\section{Lens Makers Equation}
\label{\detokenize{physics:lens-makers-equation}}
\sphinxAtStartPar
The general form of the \index{lens makers equation@\spxentry{lens makers equation}}lens makers equation:
\begin{equation*}
\begin{split}\frac{1}{f} = (n-1) \left[ \frac{1}{R_1} - \frac{1}{R_2} + \frac{(n-1)d}{n R_1 R_2} \right]\end{split}
\end{equation*}
\sphinxAtStartPar
where:
\begin{itemize}
\item {} 
\sphinxAtStartPar
\(n\)  is the index of refraction,

\item {} 
\sphinxAtStartPar
\(f\)   the lens’ focal lengths,

\item {} 
\sphinxAtStartPar
\(R_1\) is the \sphinxstylestrong{radius of curvature} of the surface towards the object,

\item {} 
\sphinxAtStartPar
\(R_2\) is the radius of curvature of the surface towards the sensor, and

\item {} 
\sphinxAtStartPar
\(d\)   is the thickness of the lens

\end{itemize}

\sphinxAtStartPar
See \sphinxhref{https://en.wikipedia.org/wiki/Lens\#Lensmaker's\_equation}{Wikipedia’s Lens Makers Equation}.

\sphinxAtStartPar
Thin Lens Equation:

\sphinxAtStartPar
In practice the thin lens equation:
\begin{equation}\label{equation:physics:thinlens}
\begin{split}\frac{1}{f} = \frac{1}{S_1} + \frac{1}{S_2}\end{split}
\end{equation}

\section{Snell’s Law}
\label{\detokenize{physics:snell-s-law}}\begin{equation*}
\begin{split}\frac{\sin\theta_2}{\sin\theta_1} =  \frac{n_1}{n_2}
 =\frac{v_2}{v_1}\end{split}
\end{equation*}
\sphinxAtStartPar
where:

\sphinxAtStartPar
TODO: This needs to be verified the image names match the labels.
\begin{itemize}
\item {} 
\sphinxAtStartPar
\(\theta_x\) are the angles involved.

\item {} 
\sphinxAtStartPar
\(n\)  is the index of refraction,

\item {} 
\sphinxAtStartPar
\(v\)  is the speed of propagation

\end{itemize}

\section{Reflection}
\label{\detokenize{physics:reflection}}
\sphinxAtStartPar
The \index{OVIO slit@\spxentry{OVIO slit}}OVIO slit is not an air slit. Internal reflection
tends to scramble the beam at this point.

\begin{figure}[htbp]
\centering
\capstart

\noindent\sphinxincludegraphics[scale=0.4]{{xxrefractionlaw1}.png}
\caption{Total reflection (mirror).}\label{\detokenize{physics:id3}}\end{figure}

\begin{figure}[htbp]
\centering
\capstart

\noindent\sphinxincludegraphics[scale=0.4]{{xxrefractionlaw2}.png}
\caption{Reflection from a glass surface, portion of the I:subscript:\sphinxtitleref{0} is lost.}\label{\detokenize{physics:id4}}\end{figure}

\begin{figure}[htbp]
\centering
\capstart

\noindent\sphinxincludegraphics[scale=0.4]{{xxrefractionlaw3}.png}
\caption{Exit angle refraction. (The other side of the slit substrate.)}\label{\detokenize{physics:id5}}\end{figure}

\begin{figure}[htbp]
\centering
\capstart

\noindent\sphinxincludegraphics[scale=0.4]{{xxrefractionlaw4}.png}
\caption{Total internal reflection.}\label{\detokenize{physics:id6}}\end{figure}

\sphinxAtStartPar
TODO: refine this section.

\sphinxAtStartPar
The \sphinxhref{http://hyperphysics.phy-astr.gsu.edu/hbase/phyopt/freseq.html}{calculator} at:

\sphinxAtStartPar
helps to calculate the pertinent values. A f/5 beam is the arctan(1/5)
= 11.30 degrees. Divided by 2 gives 5.65 degrees \textendash{} from the optical
axis to the side of the converging cone. With n$_{\text{1}}$ =
1.0001 (air) and n$_{\text{2}}$ = 1.53 (BK7\sphinxhyphen{}ish).

\sphinxAtStartPar
s\sphinxhyphen{}polarized:
\begin{equation*}
\begin{split}R_\mathrm{s} = \left|\frac{Z_2 \cos \theta_\mathrm{i} - Z_1 \cos \theta_\mathrm{t}}{Z_2 \cos \theta_\mathrm{i} + Z_1 \cos \theta_\mathrm{t}}\right|^2\end{split}
\end{equation*}
\sphinxAtStartPar
p\sphinxhyphen{}polarized
\begin{equation*}
\begin{split}I = I_0 \frac{ 1+\cos^2 \theta }{2 R^2} \left( \frac{ 2 \pi }{ \lambda } \right)^4 \left( \frac{ n^2-1}{ n^2+2 } \right)^2 \left( \frac{d}{2} \right)^6\end{split}
\end{equation*}
\sphinxAtStartPar
TODO: \sphinxurl{https://en.wikipedia.org/wiki/Total\_internal\_reflection\#/media/File:Total\_internal\_reflection\_by\_fluorescence.jpg}

\sphinxAtStartPar
Using the \sphinxhref{https://www.schott.com/d/advanced\_optics/c36214d9-13c4-468c-bf40-8d438b89f532/1.30/schott-optical-glass-pocket-catalog-jan-2020-row.pdf}{Shott Pocket Catalog}

\sphinxAtStartPar
A point source (star) receives information from the entire aperture with
a slight distortion due to its off\sphinxhyphen{}axis relationship. For spectroscopy,
careful centering and alignment of the ‘target’ position on the slit
onto a co\sphinxhyphen{}aligned optical axis keeps the noise symmetric. Off\sphinxhyphen{}axis
star means asymmetric line profiles at the sensor. Slight, but there.

\sphinxAtStartPar
In considering the \sphinxhref{https://en.ovio-optics.com/media/pim/assets/DocumentsPDF/std.lang.all/2-/en/Notice-Ovio-204012-EN.pdf}{OVIO} slit with a beam consisting a pencil of rays
(bundle of rays \textendash{} each with a different approach angle to the
surface). Using the above equations it is easy to see that the f/ratio
is altered significantly as each ray enters, passes, and exits the
slit’s substrate. There is a condition where internal reflection adds
an additional ray with changed geometry.  This amounts to noise in the
system. It is not a true caustic.

\section{Grating Equation}
\label{\detokenize{physics:grating-equation}}\begin{equation}\label{equation:physics:grating}
\begin{split}\frac{m\lambda}{d} = sin(\alpha) \pm sin(\beta)\end{split}
\end{equation}
\sphinxAtStartPar
where \(\lambda\) is the wavelength, \(\alpha\) is the angle
of incidence, \(\beta\) is the diffracted angle (the dependent
variable of real interest). The sign \(\pm\) is positive for
reflection gratings and negative for transmission grating. The angle
\(\phi = |\alpha| + |\beta|\) defines the main geometry of the
system.

\section{Spot Size and Slit Selection}
\label{\detokenize{physics:spot-size-and-slit-selection}}
\sphinxAtStartPar
In practice, the focal length drives the platescale eq: \eqref{equation:physics:pixelscale}
and aperture drives resolution \eqref{equation:physics:RayleighEquation}.

\sphinxAtStartPar
In general, the \index{spot\sphinxhyphen{}size@\spxentry{spot\sphinxhyphen{}size}}spot\sphinxhyphen{}size is independent of the aperture, and
wholly dependent on the focal length. Since f/ratio is a derived value
\textendash{} equation eq: \eqref{equation:physics:pixelscale} bypasses the aperture and gives a result
as a fraction of an arcsecond per micron at the focal plane:
\begin{equation}\label{equation:physics:pixelscale}
\begin{split}\frac{206204.8}{fl\times 1000} = \frac{x^"}{1 \mu{m}}\end{split}
\end{equation}
\sphinxAtStartPar
This is a elementary school ratio problem: where \(206204.8\) is
the number of arc\sphinxhyphen{}seconds in a radian; \(fl\) is the focal length
in mm (traditionally stated) and multiplied by 1000 to turn into
microns; \(x^"\) is “x” in arc\sphinxhyphen{}seconds; the goal of \(1 \mu{m}\)
relates to both pixel size and slit width.

\sphinxAtStartPar
In spectroscopy, the Rayleigh equation eq: \eqref{equation:physics:RayleighEquation} provides
a critical estimate of the ability to separate the light from two
close objects.
\begin{equation}\label{equation:physics:RayleighEquation}
\begin{split}\theta = 1.22\;\frac{\lambda}{D}\end{split}
\end{equation}
\sphinxAtStartPar
where \(\theta\) is the resolution IN RADIANS; \(1.22\) is the
first Bessel J coefficient; \(\lambda\) is the wavelength in units
of D; and \(D\) is the diameter of the aperture. For
back\sphinxhyphen{}of\sphinxhyphen{}the\sphinxhyphen{}envelope estimates, use 5e\sphinxhyphen{}5 (\(5\times 10^{-5}\)) as
the wavelength in {[}cm{]} and express D in matching units {[}cm{]}.

\sphinxAtStartPar
\sphinxstylestrong{Observation:} The width of the slit dominates resolution within the
spectroscope. The aperture requirement stresses the need for flux over
resolution. A short focal length stresses the need for a small “spot
size”, allowing a smaller slit width; in turn driving higher resolution.

\sphinxAtStartPar
The so\sphinxhyphen{}called ‘diffraction limited’ requirement of one arcsecond for
stations deep in the atmosphere only requires an aperture of around
12.58 cm (4.95 inches). This is all that is satisfy most amateur
needs under above average seeing conditions.

\section{Sellmeier Equation}
\label{\detokenize{physics:sellmeier-equation}}
\sphinxAtStartPar
The \index{Sellmeier Equation@\spxentry{Sellmeier Equation}}Sellmeier Equation, uses an empirical equation to model the
dispersion of light in medium with a given refractive index.

\sphinxAtStartPar
Values may be found at \sphinxcite{references:polyanskiy-2021}: \sphinxhref{https://refractiveindex.info/}{Refractive Index Database}
\begin{equation}\label{equation:physics:sellmeier1}
\begin{split}n^2(\lambda) = 1 + \sum_i \frac{B_i \lambda^2}{\lambda^2 - C_i}\end{split}
\end{equation}
\sphinxAtStartPar
In practice, a small handful of empirical constants determines a
workable solution to path\sphinxhyphen{}times for lenses:
\begin{equation}\label{equation:physics:sellmeier2}
\begin{split}\lambda = 1 + \frac{B_1 \lambda^2 }{ \lambda^2 - C_1}
   + \frac{B_2 \lambda^2 }{ \lambda^2 - C_2}
   + \frac{B_3 \lambda^2 }{ \lambda^2 - C_3}\end{split}
\end{equation}
\sphinxAtStartPar
Coefficients may be had from several sources:
\begin{quote}

\begin{savenotes}\sphinxattablestart
\centering
\begin{tabulary}{\linewidth}[t]{|T|T|}
\hline

\sphinxAtStartPar
B\_1
&
\sphinxAtStartPar
1.03961212
\\
\hline
\sphinxAtStartPar
B\_2
&
\sphinxAtStartPar
0.231792344
\\
\hline
\sphinxAtStartPar
B\_3
&
\sphinxAtStartPar
1.01046945
\\
\hline
\sphinxAtStartPar
C\_1
&
\sphinxAtStartPar
6.00069867 x 10\textasciicircum{} 3 microns
\\
\hline
\sphinxAtStartPar
C\_2
&
\sphinxAtStartPar
2.00179144 x 10\textasciicircum{}\sphinxhyphen{}2 microns
\\
\hline
\sphinxAtStartPar
C\_3
&
\sphinxAtStartPar
1.03560653 x 10\textasciicircum{} 2 microns
\\
\hline
\end{tabulary}
\par
\sphinxattableend\end{savenotes}
\end{quote}

\section{Scattering}
\label{\detokenize{physics:scattering}}
\sphinxAtStartPar
In optical spectroscopy the wavelength ranges from 3300\sphinxhyphen{}12,000 Angstroms
or .33 to 1.2 microns. Particles or defects in the optics may be
modeled by \sphinxcode{\sphinxupquote{\textbackslash{}sigma = 2\textbackslash{}pi\textbackslash{}r/\textbackslash{}lambda}}. Rayleigh scattering occurs when
\sphinxcode{\sphinxupquote{\textbackslash{}sigma \textless{}\textless{} 1}} and \sphinxcode{\sphinxupquote{\textbackslash{}sigma \textless{}\textless{} \textbackslash{}lambda/10}}.
\begin{equation}\label{equation:physics:RayleighIntensity}
\begin{split}I &= I_0 \frac{ 1+\cos^2 \theta }{2 R^2} \left( \frac{ 2 \pi }{ \lambda } \right)^4 \left( \frac{ n^2-1}{ n^2+2 } \right)^2 \left( \frac{d}{2} \right)^6\end{split}
\end{equation}
\sphinxAtStartPar
\textless{}ref\textgreater{}Seinfeld, John H. and Pandis, Spyros N. (2006) ‘’Atmospheric Chemistry and Physics, 2nd Edition’’, John Wiley and Sons, New Jersey, Chapter 15.1.1, \{\{ISBN|0471720186\}\}\textless{}/ref\textgreater{}
\begin{equation}\label{equation:physics:RayleighScattering}
\begin{split}\sigma_\text{s} &= \frac{ 2 \pi^5}{3} \frac{d^6}{\lambda^4} \left( \frac{ n^2-1}{ n^2+2 } \right)^2\end{split}
\end{equation}
\sphinxAtStartPar
\sphinxcode{\sphinxupquote{Siegel, R., Howell, J.R., (2002). {[}https://cds.cern.ch/record/1505325/files/9781439805336\_TOC.pdf \textquotesingle{}\textquotesingle{}Thermal radiation heat transfer\textquotesingle{}\textquotesingle{}{]}. p. 480. New York, NY: Taylor \& Francis. \{\{ISBN|1560329688\}\}}}

\section{Lambertian Reflection:}
\label{\detokenize{physics:lambertian-reflection}}
\sphinxAtStartPar
One \index{calibration lamp@\spxentry{calibration lamp}}calibration lamp method involves flooding the guider/slit chamber with
light from an off\sphinxhyphen{}axis lamp. Experiments (Rodda/Yeager) showed variation
in lamp placement had a significant impact in calibration line placement
on the spectrum. Here is the simple case of light from a bulb radiating
outwards. If the lamp is replaced with a patch of the reflecting area
inside the chamber; and considering all contributions from the entire
area of the chamber \textendash{} it is easy to see where the off\sphinxhyphen{}axis contributions
originate.  TODO Add reference to the ‘Greg’s device’.

\begin{figure}[htbp]
\centering
\capstart

\noindent\sphinxincludegraphics[scale=0.3]{{576px-Lambert_Cosine_Law_1}.png}
\caption{Relationship of reflection to solid angle \(\Omega\). (Wikipedia)}\label{\detokenize{physics:id7}}\end{figure}
\begin{equation}\label{equation:physics:Lambert-1}
\begin{split}F_{tot} &= \int\limits_0^{2\pi}\;\int\limits_0^{\pi/2}\cos(\theta)I_{max}\; \sin(\theta)\;\mathbf{d}\theta\;\mathbf{d}\phi \\
&= 2\pi\cdot I_{max}\int\limits_0^{\pi/2}\cos(\theta)\sin(\theta)\;\mathbf{d}\theta \\
&= 2\pi\cdot I_{max}\int\limits_0^{\pi/2}\frac{\sin(2\theta)}{2}\;\mathbf{d}\theta\end{split}
\end{equation}
\sphinxAtStartPar
Using \sphinxhref{https://www.wolframalpha.com}{Wolfram Alpha web site} :

\begin{sphinxVerbatim}[commandchars=\\\{\}]
integrate sin (2x / 2) dx from x = 0 to pi/2
\end{sphinxVerbatim}
\begin{equation*}
\begin{split}\int_0^{\pi/2} sin (2x / 2)\; \mathbf{d}x = 1\end{split}
\end{equation*}

\section{Thermal Expansion}
\label{\detokenize{physics:thermal-expansion}}
\sphinxAtStartPar
In general the degree of thermal expansion is \(\propto\) inverse
of the melting point. In practice the ODE
\begin{equation}\label{equation:physics:ThermalExpansionODE}
\begin{split}\alpha_{L} = \frac{1}{L}\; \frac{\mathbf{d}L}{\mathbf{d}T}\end{split}
\end{equation}
\sphinxAtStartPar
where \(L\) is the length \(T\) is in units of temperature.
FlexSpec 1 uses MKS, so coefficients here are in \(\mu{m}/m/K\).

\begin{savenotes}\sphinxattablestart
\raggedright
\sphinxcapstartof{table}
\sphinxthecaptionisattop
\sphinxcaption{Material Thermal Coefficients}\label{\detokenize{physics:id8}}
\sphinxaftertopcaption
\begin{tabular}[t]{|\X{50}{65}|\X{15}{65}|}
\hline
\sphinxstyletheadfamily 
\sphinxAtStartPar
Standard Material
&\sphinxstyletheadfamily 
\sphinxAtStartPar
Coefficient
\\
\hline
\sphinxAtStartPar
Aluminum
&
\sphinxAtStartPar
23.1
\\
\hline
\sphinxAtStartPar
Brass
&
\sphinxAtStartPar
19
\\
\hline
\sphinxAtStartPar
Carbon steel
&
\sphinxAtStartPar
10.8
\\
\hline
\sphinxAtStartPar
Invar
&
\sphinxAtStartPar
1.2
\\
\hline
\sphinxAtStartPar
Douglas\sphinxhyphen{}fir
&
\sphinxAtStartPar
3.5
\\
\hline&\\
\hline
\sphinxAtStartPar
3D FILAMENTS
&
\sphinxAtStartPar
3D FIBER COEFFICIENTS
\\
\hline
\sphinxAtStartPar
ABS
&
\sphinxAtStartPar
90
\\
\hline
\sphinxAtStartPar
ASA
&
\sphinxAtStartPar
98
\\
\hline
\sphinxAtStartPar
Carbon Fiber Filled
&
\sphinxAtStartPar
57.5
\\
\hline
\sphinxAtStartPar
Flexible
&
\sphinxAtStartPar
157
\\
\hline
\sphinxAtStartPar
HIPS
&
\sphinxAtStartPar
80
\\
\hline
\sphinxAtStartPar
Metal Filled
&
\sphinxAtStartPar
33.75
\\
\hline
\sphinxAtStartPar
Nylon
&
\sphinxAtStartPar
95
\\
\hline
\sphinxAtStartPar
PETG
&
\sphinxAtStartPar
60
\\
\hline
\sphinxAtStartPar
PLA
&
\sphinxAtStartPar
68
\\
\hline
\sphinxAtStartPar
PVA
&
\sphinxAtStartPar
85
\\
\hline
\sphinxAtStartPar
Polycarbonate
&
\sphinxAtStartPar
69
\\
\hline
\sphinxAtStartPar
Polyproplyne
&
\sphinxAtStartPar
150
\\
\hline
\sphinxAtStartPar
Wood Filled
&
\sphinxAtStartPar
30.5
\\
\hline
\end{tabular}
\par
\sphinxattableend\end{savenotes}

\sphinxAtStartPar
\sphinxhref{https://www.simplify3d.com/support/materials-guide/properties-table/}{Simply3D Table} has lots of properties related to 3D printer filaments.

\sphinxAtStartPar
TODO: Young’s Modulus.
Same issues in every spectrograph

\sphinxAtStartPar
Things we did to minimize.

\sphinxAtStartPar
Binding within spectrograph. \sphinxhyphen{}\textgreater{} distortion.

\sphinxAtStartPar
Answer is do lots of cals.

\sphinxAtStartPar
\sphinxurl{https://www.simplify3d.com/support/materials-guide/properties-table/}

\chapter{Mathematics}
\label{\detokenize{mathematics:mathematics}}\label{\detokenize{mathematics::doc}}
\sphinxAtStartPar
While exploring the physics of optics for the FlexSpec1 we encountered
aspects of mathematics tailored to optics. This section is a collection
of notes that guided our intuition to close the gaps between the theory
and the images we obtained with practice.
\begin{itemize}
\item {} 
\sphinxAtStartPar
\sphinxstylestrong{“Conventions”} get in the way of the pure math.

\item {} 
\sphinxAtStartPar
\sphinxstylestrong{Beware}! Trig \sphinxstylestrong{folds} quadrants!

\item {} 
\sphinxAtStartPar
Angles are measured as positive in a counter\sphinxhyphen{}clockwise direction, and negative in a clockwise direction using the “\index{right\sphinxhyphen{}hand\sphinxhyphen{}rule@\spxentry{right\sphinxhyphen{}hand\sphinxhyphen{}rule}}right\sphinxhyphen{}hand\sphinxhyphen{}rule”.

\end{itemize}

\sphinxAtStartPar
Most calculators and the human brain operate within the social
convention of “degrees”. Computer languages, for the most part, work
with radians. High school trigonometry has left most people with a
morbid fear of radians. When radians are used in their simplest terms
they offer a powerful shortcut to intuition for
back\sphinxhyphen{}of\sphinxhyphen{}the\sphinxhyphen{}envelope (\index{BOTE@\spxentry{BOTE}}BOTE) work.

\sphinxAtStartPar
The slope\sphinxhyphen{}intercept equation from high school algebra
\index{equation@\spxentry{equation}!slope\sphinxhyphen{}intercept@\spxentry{slope\sphinxhyphen{}intercept}}equation;slope\sphinxhyphen{}intercept uses a “rise\sphinxhyphen{}over\sphinxhyphen{}run”
\index{mathematics@\spxentry{mathematics}!rise\sphinxhyphen{}over\sphinxhyphen{}run@\spxentry{rise\sphinxhyphen{}over\sphinxhyphen{}run}}mathematics;rise\sphinxhyphen{}over\sphinxhyphen{}run paradigm that amounts to the
tangent: \(sin/cos\). The sin/cos projection winds up inside the
unit circle at the \(cos(\theta)\) position, while the tangent is
outside the unit circle and goes to infinity as \(cos(\theta)
\rightarrow\;0\). The radian measure follows the unit circle and
represents an exact value. The tangent starts at 0 degrees (and
radians) and follows a line tangent to the outside of the unit circle.

\section{Radians}
\label{\detokenize{mathematics:radians}}
\sphinxAtStartPar
With a spectrograph, the separation between two wavelengths, \(\lambda\)
and \(\lambda+\Delta{\lambda}\) may be calculated by simply (ha!)
differentiating the \index{grating equation@\spxentry{grating equation}}grating equation. The goal is to state
dispersion in units of scale instead of units of wavelength:
\begin{equation}\label{equation:mathematics:ChainRule1}
\begin{split}\frac{\tt{d}\lambda}{\tt{d}x} &= \frac{\tt{d}\lambda}{\tt{d}\beta} \\
            &= \frac{\tt{d}\lambda}{\tt{d}\beta} \frac{\tt{d}\beta}{\tt{d}x}\end{split}
\end{equation}
\sphinxAtStartPar
where \(\tt{d}x\) is the distance from the grating towards the
sensor.

\sphinxAtStartPar
The farther the camera lens is from the grating, the higher the resolution
at the cost of dimmer light.

\section{Angles}
\label{\detokenize{mathematics:angles}}
\sphinxAtStartPar
Angles \index{Angles@\spxentry{Angles}!measurement@\spxentry{measurement}}Angles;measurement are measured in a plane, taken as a
counter\sphinxhyphen{}clockwise rotation around a normal vector to the plane. In the
Cartesian coordinate system/plane, values start at zero at the
\(X\) axis and increase as the rotation goes from \(X\),
through \(Y\). The angle value wraps at zero and repeats. Negative
angles are simply those that move clockwise from zero.

\sphinxAtStartPar
Trigonometric identities “fold values” in their quadrants and pose a
number of computational problems for algorithms. For example,
\(Y=sin(X) = 0.5\) occurs at both positive and negative
\(\pi/6\) or 30 degrees. Similarly \(Y=cos(X)=0.5\) occurs
at \(\pi/3\) or 60 degrees. In other words, ambiguous results
unless one accounts for circumstances. The cross product returns
a vector normal to the plane of rotation, and with a sign representing
the direction of rotation. The magnitude of the vector can be turned
into exactly one angle. The magnitude of the angle is between \(0\) and
\(pi\) BUT the sign allows for the angle to move backwards from zero!
thus \(2\pi\) \sphinxhyphen{} alpha can take on value \(\pi < \alpha < 2\pi\)
without confusion.

\sphinxAtStartPar
This angle ambiguity is critical to computing solutions in spectroscopy.

\sphinxAtStartPar
To further complicate things

\section{Small Angle Approximation}
\label{\detokenize{mathematics:small-angle-approximation}}
\sphinxAtStartPar
Kahan \sphinxcite{references:kahan-1999} recommends the use of vectors over trig for the computation
of small angles.

\sphinxAtStartPar
Estimating accuracy of the \index{small angle approximation@\spxentry{small angle approximation}}small angle approximation, taking a
McClaurian series at face value (Taylor’s Theorem around \(x=0\)),
\begin{equation}\label{equation:mathematics:SmallAngleApproximation}
\begin{split} \sin \theta &= \sum^{\infty}_{n=0} \frac{(-1)^n}{(2n+1)!} \theta^{2n+1} \\
    &= x - \frac{x^3}{3!} + \frac{x^5}{5!} - \cdots\quad\text{ for all } x\! \\\end{split}
\end{equation}
\sphinxAtStartPar
Setting the second term \(\;\theta^3\;/\;3! > 1\;/\;206264.8\)
gives an error approximation for 1 arcsecond. (There are 206264.8 arc\sphinxhyphen{}seconds in a radian.)
Looking for an error of 1 arcsecond and solving for \(\theta\):

\section{Gaussian}
\label{\detokenize{mathematics:gaussian}}
\sphinxAtStartPar
Normalized curves are used to match and measure effective width of
spectral lines. The process of producing a line is Gaussian in nature,
dominated by Maxwell\sphinxhyphen{}Boltzmann distribution but influenced by local
physics. Other curves include the Lorenzian and the Voigt profiles.
The Voigt profile is a combination of the Gaussian and lorenzian.
The math related to the Gaussian has aspects that make it attractive
for computation.

\sphinxAtStartPar
The Gaussian, and a few derivatives are:
\begin{equation}\label{equation:mathematics:Gaussian1}
\begin{split} y(x) &= a exp^\Big(  (\frac{x-\bar{x})^{2}}{\sigma}  \Big) \\
 y^{\prime}(x) &= -\frac{2a(x-\bar{x}}{\sigma}exp^\Big(  (\frac{x-\bar{x})^{2}}{\sigma}  \Big) \\
 y^{\prime\prime}(x) &= 2\frac{a}{\sigma^{2}} \left(-\sigma + 2(x-\bar{x})^{2} \right) exp^\Big(  (\frac{x-\bar{x})^{2}}{\sigma}  \Big)\end{split}
\end{equation}
\sphinxAtStartPar
where \(a\) is the maximum occurring at \(x = \bar{x}\), \(\sigma\) is
the variance.

\sphinxAtStartPar
The inflection points are minimum at \(\bar{x}\) and
maximum at \(x=\bar{x}\pm\sqrt{\sigma/2}\).

\sphinxAtStartPar
In general fitting a Gaussian to a PSF for a star, allows cosmic ray
and sensor defects to be corrected \textendash{} remembering to account for the
error associated with those corrections.

\sphinxAtStartPar
Derivative:
\begin{equation}\label{equation:mathematics:GaussianDerivative}
\begin{split}\frac{d}{dx} e^{\frac{-ax}{\sigma}}  =  -a/c e^{\frac{-ax}{\sigma}}\end{split}
\end{equation}

\section{Fourier Transform}
\label{\detokenize{mathematics:fourier-transform}}\begin{equation}\label{equation:mathematics:Fourier1}
\begin{split}f(x) &= \int_{-\infty}^{\infty} f(\xi) e^{2 \pi i} \textrm{d}\xi\\\end{split}
\end{equation}
\sphinxAtStartPar
Note:
\begin{equation}\label{equation:mathematics:Fourier2}
\begin{split}e^{2\; \pi i x} = e^{ax}\end{split}
\end{equation}
\sphinxAtStartPar
where \(a = 2 \pi i\).

\section{Parallactic Angle}
\label{\detokenize{mathematics:parallactic-angle}}
\sphinxAtStartPar
The essential aspect of compensating for the parallactic angle is
handled in FlexSpec1 by using the Inertial Measurement Unit of an
include Nano 33 BLE Sense (or IoT) processor. By choosing an axis,
we simply make it ‘balanced’ w.r.t. the Earth’s gravity vector.
A little vector mathematics tells us the minimal direction to rotate
and some book\sphinxhyphen{}keeping tells us to avoid cable wrap.

\chapter{FlexSpec 1 Guiding}
\label{\detokenize{guiding:flexspec-1-guiding}}\label{\detokenize{guiding::doc}}
\begin{figure}[htbp]
\centering
\capstart

\noindent\sphinxincludegraphics{{m29_onesecodn_astrometry_net}.jpeg}
\caption{Example 1\sphinxhyphen{}second raw guider exposure of M29, taken 2021\sphinxhyphen{}04\sphinxhyphen{}15, A. Rodda. Platesolved by nova.astrometry.net, image from ds9.}\label{\detokenize{guiding:id1}}\label{\detokenize{guiding:rawguide1}}\end{figure}

\begin{figure}[htbp]
\centering
\capstart

\noindent\sphinxincludegraphics{{ZoomDistortion1}.jpeg}
\caption{Zoom into a guider image, showing astigmatism arising from the misalignment of the slit and guider mirror.}\label{\detokenize{guiding:id2}}\end{figure}

\sphinxAtStartPar
The \index{FS1 guiding module@\spxentry{FS1 guiding module}}FS1 guiding module addresses matching wide field of view
surrounding the slit. This provides the opportunity to acquire the
target with an imprecise slew, plate\sphinxhyphen{}solve the image for precise
positioning and to increase the chances of having a brighter off\sphinxhyphen{}slit
star for alternative guiding. We applied the lens\sphinxhyphen{}makers formula to
create a compound 2\sphinxhyphen{}element “transfer lens” solution.  The equation
\begin{equation*}
\begin{split}\frac{206264.8}{\tt{fl}\times 1000} = \frac{\tt{Magic Number}}{1 \mu{m}}\end{split}
\end{equation*}
\sphinxAtStartPar
yields the “\index{Magic Number@\spxentry{Magic Number}}Magic Number” in units of arc\sphinxhyphen{}seconds per micron for a
telescope with a focal length of \({\tt{fl}}\) in units of mm. This
equation allows computing/planning the \index{slit width@\spxentry{slit width}!matching@\spxentry{matching}}slit width;matching in terms of
arc\sphinxhyphen{}seconds of seeing. Matching the slit width to the OTA magnification
and seeing is critical to acquire the best signal, limit the sky
contributions and to mitigate the effects of atmospheric refraction
(see Parallactic Angle and Rotation ref\{sec:Rotator\}.

\sphinxAtStartPar
In imaging, multiplying the number by the pixel size in microns,
yields the arc\sphinxhyphen{}seconds per pixel. Further multiplication by the size of
the chip yields the total field of view for the image. This number
should be permanently affixed to the OTA.

\index{calculation@\spxentry{calculation}!pixel size@\spxentry{pixel size}}\index{calculation@\spxentry{calculation}!slit width@\spxentry{slit width}}\ignorespaces 
\sphinxAtStartPar
The \index{lens makers equation@\spxentry{lens makers equation}}lens makers equation:

\sphinxAtStartPar
(DIAGRAM)
\begin{equation*}
\begin{split}\frac{1}{fl} = \frac{1}{s_{1}} + \frac{1}{s_{2}} \label{E:LensMakersEquation}\end{split}
\end{equation*}
\sphinxAtStartPar
is chained together for each lens in the set to match the computed
platescale on the slit to the chip size of the camera.

\sphinxAtStartPar
(EXAMPLE IMAGE).

\section{Preliminaries}
\label{\detokenize{guiding:preliminaries}}
\sphinxAtStartPar
Take a small series \index{calibration exposures@\spxentry{calibration exposures}}calibration exposures, flats, zeros and
darks for the guide camera. \index{FS1 slit carousel@\spxentry{FS1 slit carousel}}FS1 slit carousel has one position
filled to serve as a general \index{shutter@\spxentry{shutter}}shutter for dark exposures.
\begin{enumerate}
\sphinxsetlistlabels{\arabic}{enumi}{enumii}{}{.}%
\item {} 
\sphinxAtStartPar
Take zeros and darks, flats and make masters

\item {} 
\sphinxAtStartPar
Solve for defects: \((x,y)\).

\item {} 
\sphinxAtStartPar
Slew to field

\item {} 
\sphinxAtStartPar
Take a few long exposures (10sec?) to reach mag 15

\item {} 
\sphinxAtStartPar
Correct images darks/flats/defects

\item {} 
\sphinxAtStartPar
Identify main stars and platesolve.

\item {} 
\sphinxAtStartPar
Illuminate the slit from behind.

\item {} 
\sphinxAtStartPar
Solve the slit position (\(y = mx+b\))

\end{enumerate}

\sphinxAtStartPar
For the slit:
\begin{enumerate}
\sphinxsetlistlabels{\arabic}{enumi}{enumii}{}{.}%
\item {} 
\sphinxAtStartPar
The slit has rotated.

\item {} 
\sphinxAtStartPar
Position a point\sphinxhyphen{}source onto the ‘old’ best position.

\item {} 
\sphinxAtStartPar
Science image.

\item {} 
\sphinxAtStartPar
Solve the ‘Y’ offset of point source.

\item {} 
\sphinxAtStartPar
Recalculate the guide \((x,y)\) for point source to put the dispersion axis back onto original points.

\end{enumerate}

\sphinxAtStartPar
Science Camera:
\begin{enumerate}
\sphinxsetlistlabels{\arabic}{enumi}{enumii}{}{.}%
\item {} 
\sphinxAtStartPar
Take zero/dark/flats

\item {} 
\sphinxAtStartPar
Determine the defect map \((x,y)\).

\item {} 
\sphinxAtStartPar
Determine an optimal position \((y)\) for dispersion axis based on defects.

\item {} 
\sphinxAtStartPar
Record the position.

\end{enumerate}

\chapter{Remote Protocol}
\label{\detokenize{protocol:remote-protocol}}\label{\detokenize{protocol::doc}}
\sphinxAtStartPar
The control structure is being developed in a platform agnostic network
neutral fashion leveraging web applications (web apps) via bokeh and
other tools.

\sphinxAtStartPar
The bokeh server is a Raspberry Pi and is be considered to be the
‘main’ computer, a peer in an asynchronous distributed network of
peers. Any SBC/Desktop computer with a decent operating system may be
used for the server. The ODroid, BeagleBone, Intel NUC etc. Some SBC
\index{SBC@\spxentry{SBC}!Configuration@\spxentry{Configuration}}SBC;Configuration configuration will be required.

\sphinxAtStartPar
Arduino class devices are designated as an SBM is a “Single Board
Microcontroller”.

\sphinxAtStartPar
This approach sticks with the Arduino control system (boots out of the
box) and does not use an after\sphinxhyphen{}marker RTOS or PyCharm.

\sphinxAtStartPar
The essential parts:
\begin{itemize}
\item {} 
\sphinxAtStartPar
The actual hardware at the interface of the SBM and the real world,
where the if/then/else/switch/maths part is next to the
hardware. Timing may exist here.

\item {} 
\sphinxAtStartPar
The logical element within the Arduino for a part: A ‘StepperMotor’ may
have several ways to do things, there may be several different steppers
in a device. Handles the commands and is a communications terminus
or originator of status etc back to its manager.

\item {} 
\sphinxAtStartPar
The Raspberry Pi/Odroid/Linux box that owns the serial wires. Actual
wires.

\item {} \begin{description}
\item[{The user interface:}] \leavevmode\begin{itemize}
\item {} 
\sphinxAtStartPar
People via interaction a browser with buttons etc…

\item {} 
\sphinxAtStartPar
A controller program like a scheduler

\item {} 
\sphinxAtStartPar
(both at the same time)

\end{itemize}

\end{description}

\end{itemize}

\sphinxAtStartPar
One hard part is the timing required. We don’t have any real sense
of a “timer”. We have hacked up something to help, but that control
loop gets complicated with more than one set of things to do.

\sphinxAtStartPar
The other main division is in how messages flow.
\begin{itemize}
\item {} 
\sphinxAtStartPar
A message shall only be a JSON structure. The structure will be
created by a program and therefore checked before being sent. This
requirement removes all the checking requirements in the
Arduino. The JSON message will be a single string of ASCII
characters consisting divided into two classes of characters: Case
1) special \sphinxhyphen{} the braces, colon, comma and double quote mark \{\}:,”
Case 2) The characters A\sphinxhyphen{}Za\sphinxhyphen{}z0\sphinxhyphen{}9.\_ and noting else.

\end{itemize}
\begin{description}
\item[{\sphinxstylestrong{Case 1} are filtered when messages are parsed. This makes matching the close}] \leavevmode
\sphinxAtStartPar
brace to the open brace very small in the Arduino.

\item[{\sphinxstylestrong{Case 2} Means any illegal character \textendash{} that have a remote possibility}] \leavevmode
\sphinxAtStartPar
of occurring due to a bit\sphinxhyphen{}flip in coms, can act as a trigger to reset.

\item[{A JSON structure is a “dictionary” (special collection or set) of a}] \leavevmode
\sphinxAtStartPar
“key” and a “value”. A key is restricted to being only a quoted
string and a value may be one of three things: a quoted string,
ASCII integer representation, float in the form of
whole\sphinxhyphen{}dot\sphinxhyphen{}fraction expressed.

\end{description}

\sphinxAtStartPar
The Serial communications assumes more than on SBM on a wire pair.
All listen to the wire and parse a single JSON dictionary that matches
their name. The SBM parses this dictionary and dispatches any enclosed
value JSON dictionaries to each “widget”. The widget is responsible
for understanding and acting on the content of that dictionary.
A Key is considered a class of command and its values are considered
the parameters for that action.

\sphinxAtStartPar
This next part is a trick.

\sphinxAtStartPar
There will be two “mirrored” classes: Python for the Raspberry Pi
and C++ for the SBM.

\sphinxAtStartPar
The class (Python) in the Raspberry Pi has to mirror the class in the
Arduino exactly. This allows them to communicate in their own agreed
upon way to assure proper operation. This requirement alleviates
the need for a universal grammar or command set.

\sphinxAtStartPar
The ‘format’ of the message will be 1) JSON BUT 2) the content is left
up to both sides of that class.  The Python will have Bokeh/GUI
stuff. The Arduino implements all the tedious logic to make things act
and/or move. The paradigm is one of a Navy Captain and the Chief of
the Boat: The Captain knows he wants to make a certain speed to
a target and no idea how that happens. He ‘orders’ the Chief
to make 15 knots NNE. The Cheif tells the engine room to make
a certain number of ‘revolutions’.

\sphinxAtStartPar
The GUI user does not want to think in terms of stepper\sphinxhyphen{}motor
steps, directions. They want to move to a logical position.
The Arduino receives a JSON key/value pair that might say \textendash{}
in this scenario \textendash{} \{ … “speed” : “23{[}knots{]}” … \} and
parses the value as it sees fit. The units may be implicit, as
the two classes understand how that message’s value needs to
be handled.

\sphinxAtStartPar
The Raspberry Pi Python class communicates with the ‘user’
(person/algorithm). In this case a Python web\sphinxhyphen{}app built on Bokeh, or
will simply accept and pass\sphinxhyphen{}thru messages from an algorithm user. It
lives on a Raspberry Pi, and has lots of program space to do all the
logic and format checks to guarantee the messages sent to the SBM is
correct.  (Remember remove checks from the Arduino to the degree
possible).

\sphinxAtStartPar
The Raspberry Pi owns the serial lines: RS\sphinxhyphen{}232 two\sphinxhyphen{}wire, I2C, BLE
device.  This means Serial will be a server. It is provides one access
point to all classes/programs the electrical system. It will accept
and queue messages and route them by electrical protocol.

\sphinxAtStartPar
In the code repository the Slit may look like:

\sphinxAtStartPar
FS\_Slit.h
FS\_SLit.cpp
FS\_SLit.py

\sphinxAtStartPar
They will have dependencies in other classes within the architecture,
to handle the Bokeh (Python) and the messaging (Python and Arduino).

\section{Summary:}
\label{\detokenize{protocol:summary}}
\sphinxAtStartPar
The controls/sensors may be part of the Raspberry Pi itself, using a
separate RS\sphinxhyphen{}232/I2C/Wireless/Ethernet channel to the physical bits;
They may go through RS\sphinxhyphen{}232/I2C/BLE to a Arduino SBM. Tying these
together will be in Python/C++ on the Raspberry Pi. Doing the work is a
problem left somewhere else \textendash{} but required to use this communications
scheme.

\sphinxAtStartPar
Differences with ASCOM:

\sphinxAtStartPar
We do the GUI parts inside the chain, and do not rely on templates
as shims between components. This makes fast/direct coding possible.

\section{Kzin Ring Example}
\label{\detokenize{protocol:kzin-ring-example}}
\sphinxAtStartPar
The Kzin ring example:

\begin{wrapfigure}{l}{0pt}
\centering
\noindent\sphinxincludegraphics{{KzinArduinoCommand}.png}
\caption{The Kzin ring has the ability to turn on one or more of the lamps within its purview as needed. Here NeAr, Osram (Argon only), H\sphinxhyphen{}Alpha (LED), O{[}III{]} (LED), Flat (Compo of lamps) and Blue (additional LEDs) may be chosen. The yellow area is a debug mode window showing the text to be sent by serial port to the registered LED.}\label{\detokenize{protocol:id1}}\end{wrapfigure}

\sphinxAtStartPar
The nested\sphinxhyphen{}dictionary is nested inside a distribution to the “Postmaster”
that owns the spectrograph with the Kzin ring. The “Postmaster” on the
particular Arduino dispatches to an instance of a Kzin class with
the name (Kzin) the class sends the settings to to the class using
the “Process” method. The fine details of “Process” are implemented
to set the internal state and do what is necessary to conform that internal
state to the operation of that ring. In other words, if ‘osram’ had been on
at the time “Process” was called; it will be turned off. I ‘near’ was
off it is turned on \textendash{} all within the context of this one ‘command’ to
the Kzin ring.

\sphinxAtStartPar
The details of routing are not shown, as the Bokeh class only contributes
this message and that is the text we see.

\chapter{FlexSpec 1 Ecosystem}
\label{\detokenize{controls:flexspec-1-ecosystem}}\label{\detokenize{controls:fs1-ecosystem}}\label{\detokenize{controls::doc}}
\sphinxAtStartPar
Use Case: Develop a basic GUI to Arduino Test case that will be the
basis for all Arduinos.

\begin{figure}[htbp]
\centering
\capstart

\noindent\sphinxincludegraphics{{PiggyBackBllinky}.png}
\caption{PiggyBack is the name of an Arduino, on an OTA, “piggybacked” onto
the main spectrgraph OTA. The On/Off radio buttons originate
a message down to the device. It advertises text in a SandStone
coloured box, and allows a integer value to be entered for the
Pause Rate and Cycle Count for the Blinky Object Chain.}\label{\detokenize{controls:id1}}\end{figure}

\section{Control Overview}
\label{\detokenize{controls:control-overview}}
\sphinxAtStartPar
The FlexSpec 1 is designed to live with other devices under the umbrella
of a main scheduler. This requires partitioning each subsystem, and its
components in a way that information can be shared at within the instrument,
between other instruments, shared resources at a site and between other
layers within a master scheduler. The architecture of FlexSpec 1 is open.

\begin{figure}[htbp]
\centering
\capstart

\noindent\sphinxincludegraphics{{FlexSpec_Comm_Regional}.png}
\caption{Seen from the point\sphinxhyphen{}of\sphinxhyphen{}view of the Main OTA: The Raspberry PI has three means of communication: Ethernet with the world; Serial (1.8V/Voltage management) with Arduino SBMs; I2C for short haul with SMBs and stand alone sensors. Each sub\sphinxhyphen{}system is managed by its own collection of C++/Python classes.}\label{\detokenize{controls:id2}}\end{figure}

\sphinxAtStartPar
The best way to approach the control structure is to start at the distal
end of the control message chain \textendash{} the actual component being controlled.

\sphinxAtStartPar
The component is implemented using a C++ class within the arduino. There
may be a few implementations of these classes \textendash{} depending on the
architectural type of the Arduino/other device used. C++ classes
are used, as several of the same component may appear in one FlexSpec 1
instrument. They are disambiguated using a name.

\sphinxAtStartPar
Classes consist of “data+methods”. The data is always present when
included in a compiled program. However the data portion is only
created when a class is instantiated.

\begin{figure}[htbp]
\centering
\capstart

\noindent\sphinxincludegraphics{{GUI_Hardware}.png}
\caption{The Ethernet provides a potential connection to the world. The Browser in the world serves a HTML DIV for each of the instantiated devices, shown here with a darker green background. Here we have a power block “Blinky Power” \textendash{} with lots of switches; A LowRez configuration spectrograph with its slit positioner, its grating selector and a Calibration Lamp for NeAr.}\label{\detokenize{controls:id3}}\end{figure}

\sphinxAtStartPar
In the figure, each “instantiated device”. In the case of the Slit
Positioner “Slit LoRez” a motor, that is permitted to make full
rotations. It is controlled by an instance of a C++ class running
within its controlling Arduino. It is physically wired and resides on
a multi\sphinxhyphen{}drop line. The “shim” that connects this physical device to
the outside world is an instance of a Bokeh class that translates the
HTML/JSNode events from the Browser into JSON strings to be shipped to
its associated widget within one of the arduinos attached to this
system. This is a common widely used protocol \textendash{} borrowed mostly from
the Data Visualization Community. It is extremely platform independent.

\sphinxAtStartPar
You can control your system with any enabled browser, on any device,
anywhere you are allowed to go: including NASA’s Deep Space Network.

\sphinxAtStartPar
a C++ class instance running on an arduino connected by a “RS\sphinxhyphen{}232” type interface to its controlling Arduino residing on a multi\sphinxhyphen{}drop

\sphinxAtStartPar
Scenario: Consider temperature sensors.

\begin{sphinxVerbatim}[commandchars=\\\{\}]
The generic temperature sensor: FlexTemperature
Data: string Name
Methods:
  FlexTemperature() // constructor
  FlexTemperature(const string \PYGZam{}ref)
  void status(Message\PYGZlt{}x,y\PYGZgt{} \PYGZam{}response)
  static FlexTemperature *factory(const string \PYGZam{}ref)
\end{sphinxVerbatim}

\sphinxAtStartPar
In general a non\sphinxhyphen{}initialized constructor is only supported for
development. It costs nothing in terms of the code.

\sphinxAtStartPar
The construction with initialization capability of the form
FlexTemperature(const string \&ref). The string is a narrow
subset of a JSON structure. The syntax is described

\sphinxAtStartPar
This spectrograph uses several small single board computers with a serial
protocol to control:
\begin{itemize}
\item {} 
\sphinxAtStartPar
Slit selection

\item {} 
\sphinxAtStartPar
Grating selection

\item {} 
\sphinxAtStartPar
Focus of the colliminating lens

\item {} 
\sphinxAtStartPar
Enabling one or more calibration lamps
\begin{itemize}
\item {} 
\sphinxAtStartPar
High voltage lamps require a duty cycle

\end{itemize}

\end{itemize}
\begin{quote}
\begin{itemize}
\item {} 
\sphinxAtStartPar
High intensity (boosting blue) requires short cycle times

\end{itemize}
\begin{itemize}
\item {} 
\sphinxAtStartPar
Colour LEDs to support gross grating position

\end{itemize}
\end{quote}
\begin{itemize}
\item {} 
\sphinxAtStartPar
A slit back\sphinxhyphen{}illumination lamp

\item {} 
\sphinxAtStartPar
Sensors for temperature and other aspects

\item {} 
\sphinxAtStartPar
Orientation for parallactic angle measurement

\end{itemize}

\sphinxAtStartPar
The control elements essentially boil down to:
\begin{itemize}
\item {} 
\sphinxAtStartPar
Motor

\item {} 
\sphinxAtStartPar
Sensor

\item {} 
\sphinxAtStartPar
Switch

\end{itemize}

\section{Control System}
\label{\detokenize{controls:control-system}}\label{\detokenize{controls:fs1-control}}
\sphinxAtStartPar
The critical part of the control system is the device to be control.
The devices essentially fall into three main categories:
\begin{enumerate}
\sphinxsetlistlabels{\arabic}{enumi}{enumii}{}{.}%
\item {} 
\sphinxAtStartPar
Sensor

\item {} 
\sphinxAtStartPar
Switch

\item {} 
\sphinxAtStartPar
Motor

\end{enumerate}

\section{FlexJSON \textendash{} Narrow JSON Description}
\label{\detokenize{controls:flexjson-narrow-json-description}}\label{\detokenize{controls:flexjson}}
\sphinxAtStartPar
This section was created to address the use of JSON on Arduino/
C++ environments that have very limited CPUs and small memory.
The choice of the Nano BLE Sense 33 and the Xiao do not have
these restrictions.

\sphinxAtStartPar
The character set for the JSON permitted include only
Latin\sphinxhyphen{}7 characters; useful for encoding while preserving
some “in\sphinxhyphen{}band” testing.

\sphinxAtStartPar
\sphinxhref{https://en.wikipedia.org/wiki/JSON}{JSON} (Javascript Object
Notation) provides a stateless, real\sphinxhyphen{}time peer\sphinxhyphen{}peer communications
protocol. It defines the “payload” of any communications wrapper.

\sphinxAtStartPar
JSON is well modeled by a Python Dictionary. A “dictionary” consists
of a Key:Value pair.  In the JSON world, a general restriction is to
have all characters within the string to be plain text (no ‘binary’
characters.) Integers are represented by their textual representation,
floats etc.  A JSON value may be a string, integer, float, list or
another dictionary.  It is the nested nature of the dictionary that
supports FlexSpec interoperability.

\sphinxAtStartPar
The Arduino Nano 33 BLE Sense and IoT have sufficient capability
to support the ArduinoJson library. This is well crafted to be
memory efficient.

\section{Motors}
\label{\detokenize{controls:motors}}
\sphinxAtStartPar
ELEGOO 5 Sets 28BYJ\sphinxhyphen{}48 ULN2003 5V Stepper Motor + ULN2003 Driver Board Compatible with Arduino

\sphinxAtStartPar
ULN2803 Darlington driver

\chapter{Communications}
\label{\detokenize{communication:communications}}\label{\detokenize{communication::doc}}
\sphinxAtStartPar
The main scenario \index{scenario@\spxentry{scenario}!communications@\spxentry{communications}}scenario;communications is one of:
\begin{itemize}
\item {} 
\sphinxAtStartPar
An observing network of sites (observatories)

\item {} 
\sphinxAtStartPar
Each observatory has one or more buildings

\item {} 
\sphinxAtStartPar
Each building has one or more piers

\item {} 
\sphinxAtStartPar
Each pier has its elements, and one or more OTAs

\item {} 
\sphinxAtStartPar
Each OTA has lots of things. One or more of them may be Flex Spec 1 spectrographs.

\end{itemize}

\sphinxAtStartPar
This project implements its OTAs with piggy\sphinxhyphen{}back Raspberry Pi processors
on the OTA with one power cable and one Ethernet cable. This makes wire
maintenance very easy. Since the Raspberry Pi is already deployed, with
Astroberry KStars/INDI/Ekos \textendash{} there is spare room for our instrument’s
control Single Board Microcontrollers (SBMs).

\sphinxAtStartPar
In spectroscopy it is desirable to have a piggy\sphinxhyphen{}back system for simultaneous
photometry of the target.

\sphinxAtStartPar
Each OTA may have one or more Raspberry computers. Each computer may have one or
more serial connections (multi\sphinxhyphen{}drop destinations using a serial interface)
to one or more Arduino\sphinxhyphen{}class SBMs.

\sphinxAtStartPar
Remembering the mantra, “Flexible is Flexible” \textendash{} how this gets built and
orchestrated makes for a very interesting problem.

\sphinxAtStartPar
The message origination may be a GUI like interface or an intelligent
scheduler. Ideally the scheduler is inter\sphinxhyphen{}operable with other schedulers
to maximize the observing output of its network. This is the “lofty” future goal.
Now is present\sphinxhyphen{}time for architecture.

\sphinxAtStartPar
There are two paradigms to help with understanding the FlexSpec
communication:
\begin{itemize}
\item {} 
\sphinxAtStartPar
The Captain of a Ship concept: Here directions are supplied to the crew in the form of orders in common terms (rotate n degrees) and the crew translates that into a compass heading.

\item {} 
\sphinxAtStartPar
The matryoshkas \index{matryoshkas@\spxentry{matryoshkas}}matryoshkas (nested\sphinxhyphen{}doll) model: messages within messages.

\item {} 
\sphinxAtStartPar
Postal Delivery System, with a set of inter\sphinxhyphen{}related postmasters. The postmaster accepts packages or envelopes, with a return address.

\end{itemize}

\sphinxAtStartPar
The implementation is a nested set of restricted JSON dictionaries.

\sphinxAtStartPar
A dictionary is a “key” : “value” pair. The key is restricted to always be a quoted\sphinxhyphen{}string
without spaces.  The “value” may be a quoted string, an integer (no quotes), a float
(no quotes and not using exponential notation) or \textendash{} yup a dictionary.

\sphinxAtStartPar
The idea is to have a set of “matched classes” for each widget utilized. They
are matched as:

\section{Character Set}
\label{\detokenize{communication:character-set}}
\sphinxAtStartPar
The JSON communications strings are taken from a restricted ASCII
character set ANSI X3.4\sphinxhyphen{}1986 \index{communication@\spxentry{communication}!ASCII ANSI
X3.4\sphinxhyphen{}1986@\spxentry{ASCII ANSI
X3.4\sphinxhyphen{}1986}}communication;ASCII ANSI
X3.4\sphinxhyphen{}1986 with an 8\sphinxhyphen{}bit data frame, MSB defined to be zero. This
permits traditional 8\sphinxhyphen{}bit serial terminal code (PuTTY) \index{PuTTY@\spxentry{PuTTY}}PuTTY
to monitor lines, permits using out of band characters as an alarm
for corrupted serial communications, allows special characters
(ASCII control characters) to serve allow in\sphinxhyphen{}band synchronization
and special “in\sphinxhyphen{}band” control.

\sphinxAtStartPar
Here the characters \sphinxcode{\sphinxupquote{\{\}"":,}} are strictly reserved for JSON use
to promote very restricted hand\sphinxhyphen{}coded JSON capability for lesser
machines.

\chapter{Serial Communication}
\label{\detokenize{serial:serial-communication}}\label{\detokenize{serial::doc}}

\section{Raspberry Pi}
\label{\detokenize{serial:raspberry-pi}}
\begin{figure}[htbp]
\centering
\capstart

\noindent\sphinxincludegraphics[scale=0.4]{{RPi-GPIO-Pinout-Diagram-2}.png}
\caption{Reference for GPIO pins. (Raspberrypi.org)}\label{\detokenize{serial:id1}}\end{figure}

\sphinxAtStartPar
Make sure serial is enabled via the \sphinxstylestrong{raspi\sphinxhyphen{}config} file.

\begin{sphinxVerbatim}[commandchars=\\\{\}]
sudo raspi\PYGZhy{}config
Would you like a login shell to be accessible over serial? no
Would you like the serial port hardware to be enabled? YES
Save and reboot.
\end{sphinxVerbatim}

\begin{sphinxVerbatim}[commandchars=\\\{\}]
minicom \PYGZhy{}b 115200 \PYGZhy{}o \PYGZhy{}D \PYGZlt{}Port\PYGZus{}Name\PYGZgt{}
\end{sphinxVerbatim}

\sphinxAtStartPar
\textless{}Port\_Name\textgreater{} is either /dev/ttyAMA0 or /dev/serial0

\sphinxAtStartPar
Connect pin 14 and 15 (loopback) test.
minicom or similar will work.

\sphinxAtStartPar
To check what ttys are available (Astroberry example here):

\begin{sphinxVerbatim}[commandchars=\\\{\}]
dmesg \PYG{p}{|} grep enabled \PYG{p}{|} grep \PYGZhy{}o \PYGZhy{}\PYGZhy{} \PYG{l+s+s2}{\PYGZdq{}tty[0\PYGZhy{}9]\PYGZbs{}+\PYGZdq{}}
\end{sphinxVerbatim}

\sphinxAtStartPar
Get a terminal emulator for assistance with development.

\begin{sphinxVerbatim}[commandchars=\\\{\}]
sudo apt install putty
\end{sphinxVerbatim}

\sphinxAtStartPar
Run PuTTy, and the program starts a small GUI. In the case
of the Arduino IDE, use the Tools \sphinxhyphen{}\textgreater{} Serial \sphinxhyphen{}\textgreater{} Monitor
and, in one case, the port is “/dev/ttyACM” and the rate
is “115200”.

\sphinxAtStartPar
Save the session.

\sphinxAtStartPar
“Load” a named session. Then change the font FreeMono font\sphinxhyphen{}size to 14,
background (light green to sorta imply Arduino), text color to black,
cursor to black

\sphinxAtStartPar
You can change the font sizes, colors etc
via the PuTTy GUI and save with the session. Good idea to
use different color as needed.

\sphinxAtStartPar
Attach a small Arduino, running a script to print “Hello World”
every second, and you should output. This verifies a “closed
loop” solution has been achieved with PuTTy!

\begin{wrapfigure}{l}{0pt}
\centering
\noindent\sphinxincludegraphics[scale=0.5]{{Putty}.png}
\caption{Screenshot of Putty, under Ubuntu 18.04 Xfce. Note: the Category column \textendash{} where Window Color, Fonts etc may be found and changed. Note: Saved sessions offer the ability to name a session. One may achieve a pleasing appearance by selecting TitanSerialACM0\_Arduino, then Load; change the options and resave.}\label{\detokenize{serial:id2}}\end{wrapfigure}

\sphinxAtStartPar
WARNING:

\sphinxAtStartPar
COMMON VOLTAGES FOR PINS ON Small Board Computers range across
1.8, 3.3 and 5 VOLTS. MIXING SIGNALS CAN PERMANENTLY DAMAGE
HARDWARE.

\sphinxAtStartPar
FlexSpec software supports I2C and RS\sphinxhyphen{}232 and RS\sphinxhyphen{}485 as the communication
spec. I2C is a common scheme between boards located in very close
proximity. RS\sphinxhyphen{}485 is a differential signal scheme, range just over 1
kilometer. RS\sphinxhyphen{}485 wraps a 0\sphinxhyphen{}5V signal within a common\sphinxhyphen{}mode noise
voltage range of \sphinxhyphen{}7 to 12 V ( \sphinxhyphen{}7 to (0:5 +7) = 12 V). Long hauls,
multidrop capability and noise immunity are hallmarks of the RS\sphinxhyphen{}485
protocol.

\sphinxAtStartPar
RS232, ( Telecommunications Industry Association TIA\sphinxhyphen{}232\sphinxhyphen{}F)
\begin{itemize}
\item {} 
\sphinxAtStartPar
0 (space)     Asserted        +3 to +15 V    “Computer zero”

\item {} 
\sphinxAtStartPar
1 (mark)      Passive \sphinxhyphen{}15 to \sphinxhyphen{}3 V    “Computer one”

\end{itemize}

\sphinxAtStartPar
There is a “hysteresis” of 6V absolute (\sphinxhyphen{}3 to 3) between valid
signals to differentiate noise.

\sphinxAtStartPar
The maximum voltage range is from \sphinxhyphen{}25 to 25 volts.

\begin{figure}[htbp]
\centering
\capstart

\noindent\sphinxincludegraphics[scale=0.75]{{Bokeh1Hack}.png}
\caption{The Bokeh widget uses a “has\sphinxhyphen{}a” relationship to one or more FlexServers. The FlexServer may be local to same machine or remote.  The message is passed to any subclass \textendash{} here a FlexSerial class    which owns the interface to it’s local machines serial port where  Arduino/other SBMs reside.}\label{\detokenize{serial:id3}}\end{figure}

\chapter{User Software}
\label{\detokenize{software:user-software}}\label{\detokenize{software::doc}}
\sphinxAtStartPar
The overall goal of the project is to utilize free (as in money) software
that is platform agnostic (Capable of running or being made to run) on
all operating systems. One main sub\sphinxhyphen{}goal is to create an simple architecture
using basic web enabled applications, inexpensive Single Board Computers (SBCs)
(Raspberry Pi running the Astroberry suite), inexpensive Single Board
Microprocessors (SBMs). Another sub\sphinxhyphen{}goal is to leverage the best tools
for collaboration including Github, and Sphinx \textendash{} the package that
creates this documentation tied to Readthedocs.io.

\sphinxAtStartPar
The basic philosophy is to used ‘mirrored’ object\sphinxhyphen{}oriented classes written
in Python/Bokeh for managing the instructins from its users, relaying
those instructions via JSON to C/C++ classes running on the SBM. We use
the Raspberry Pi mounted to the telescope’s OTA to offer the web interface
and to direct messages to other Pi’s and arduinos within the full instrumentation
for the Pier and its OTAs.

\section{Remote Desktop}
\label{\detokenize{software:remote-desktop}}
\sphinxAtStartPar
Many use the VNC Desktop ®, TeamViewer ®, Microsoft Remote
Desktop ® and Chromeremote ® are packages we have encountered
in the wild.

\sphinxAtStartPar
KStars/INDI/Ekos:
\begin{itemize}
\item {} 
\sphinxAtStartPar
Windows

\item {} 
\sphinxAtStartPar
Linux:
\begin{itemize}
\item {} 
\sphinxAtStartPar
Desktop

\item {} 
\sphinxAtStartPar
Raspberry/PI

\item {} 
\sphinxAtStartPar
ODroid

\end{itemize}

\item {} 
\sphinxAtStartPar
Apple

\item {} 
\sphinxAtStartPar
SAOImage/ds9 (Platform Agnostic)

\item {} 
\sphinxAtStartPar
Astrometry.net (program and )

\item {} 
\sphinxAtStartPar
Sextractor (image to data conversion)

\end{itemize}

\section{Networking}
\label{\detokenize{software:networking}}
\sphinxAtStartPar
X11/R6 The X Consortium dissolved at the end of 1996, producing a
final revision, X11R6.3. Pre\sphinxhyphen{}1983, known as “W” \textendash{} move to X in
1984, settled down to the X11 release in 1986.

\sphinxAtStartPar
Wayland, X Org people (2010\sphinxhyphen{}Current), with XWayland to tie back
to legacy systems.

\section{Serial Port Management}
\label{\detokenize{software:serial-port-management}}
\sphinxAtStartPar
The chapter on Serial Communications covers details, Putty is the
package of choice as it is platform independent.

\section{End\sphinxhyphen{}user Software}
\label{\detokenize{software:end-user-software}}
\sphinxAtStartPar
TODO Add hyperlinks

\sphinxAtStartPar
The 3D design work was done with SolidWorks ®, Autodesk Fusion/360 ®,
TinkerCad ® and special modifications made with Cura ®.

\section{Computer Languages}
\label{\detokenize{software:computer-languages}}
\sphinxAtStartPar
The two languages of this project are Python and C++. The C++ is the
GNU toolchain \textendash{} very consistent across platforms. The GNU compiler
suite has excellent language libraries. Some external libraries
for the Arduino are not the best in the world \textendash{} be careful there.

\sphinxAtStartPar
The Pythonic environment of choice include Anaconda and VSCode. The
Anaconda environment is widely used in Astronomy and the VSCode widely
used on Win10 environments. Both have advantages and disadvantages.
The main thing with Python is to match the very extensive libraries
more that sweat the language details. The libraries include numpy, astropy,
scipy etc.

\sphinxAtStartPar
Other languages include “bash”, the Linux/Unix shell. Beware, bash on
Win10 IS NOT CONSISTENT. A handful of useful Linux utilities were used
to develop code \textendash{} not needed for run\sphinxhyphen{}time support.

\section{Science}
\label{\detokenize{software:science}}
\sphinxAtStartPar
Telescope and camera management:
\begin{itemize}
\item {} 
\sphinxAtStartPar
KStars/INDI/Ekos

\item {} 
\sphinxAtStartPar
Astroberry (augmented)

\end{itemize}

\sphinxAtStartPar
Reductions were performed with
\begin{itemize}
\item {} 
\sphinxAtStartPar
BASS

\item {} 
\sphinxAtStartPar
Demetra

\item {} 
\sphinxAtStartPar
ISIS

\item {} 
\sphinxAtStartPar
VSpec

\item {} 
\sphinxAtStartPar
IRAF

\item {} 
\sphinxAtStartPar
PlotSpectra

\end{itemize}

\sphinxAtStartPar
Tools include
\sphinxhyphen{} SAOImage ds9
\sphinxhyphen{} fitsverify

\sphinxAtStartPar
General tools:
\begin{itemize}
\item {} 
\sphinxAtStartPar
Anaconda Python env, including Jupyter, Spyder etc.

\end{itemize}

\section{Bokeh/Holoviz/Panel}
\label{\detokenize{software:bokeh-holoviz-panel}}
\sphinxAtStartPar
Bokeh \sphinxhref{https://www.psych.mcgill.ca/labs/mogillab/anaconda2/lib/python2.7/site-packages/bokeh/command/subcommands/serve.py}{parameters} at McGill University.

\sphinxAtStartPar
TODO: Token

\sphinxAtStartPar
TODO: Authentication

\sphinxAtStartPar
Bokeh \sphinxhref{https://docs.bokeh.org/en/latest/docs/user\_guide/server.html}{server}
instructions.

\sphinxAtStartPar
Some additional software packages need to be installed:

\begin{sphinxVerbatim}[commandchars=\\\{\},numbers=left,firstnumber=1,stepnumber=1]
apt\PYGZhy{}get update
apt\PYGZhy{}get \PYGZhy{}y install gcc
pip3 install numpy
pip3 install astropy\PYG{o}{[}all\PYG{o}{]}
pip3 install pandas
pip3 install bokeh
\end{sphinxVerbatim}

\sphinxAtStartPar
TODO: Cite the trademarks etc.

\section{Other Packages}
\label{\detokenize{software:other-packages}}
\sphinxAtStartPar
Here is a collectin or very random links to other coding projects.

\sphinxAtStartPar
Mostly in PERL
\sphinxhref{https://github.com/robertoabraham/ProjectDragonfly/tree/master/scripts}{DragonFly}

\chapter{CAD Computer Aided Design}
\label{\detokenize{cad:cad-computer-aided-design}}\label{\detokenize{cad::doc}}
\sphinxAtStartPar
The main design cycle consists of experiments, hand sketches, capture
of the sketches into one of the main CAD packages, to produce STL
files. STL files \index{STL files@\spxentry{STL files}}STL files are converted into \sphinxcode{\sphinxupquote{gcode}} using Cura \index{Cura@\spxentry{Cura}}Cura, moved to
the printer using \sphinxcode{\sphinxupquote{Octoprint}} \index{Octoprint@\spxentry{Octoprint}}Octoprint and printed. The 3D parts are
evaluated and (altered within this cycle) as needed.

\sphinxAtStartPar
Parts are easily shared across the world, via email or the GitHub
we maintained while developing the spectrograph.

\sphinxAtStartPar
Flex Spec 1 relied heavily on cad programs:
\begin{enumerate}
\sphinxsetlistlabels{\arabic}{enumi}{enumii}{}{.}%
\item {} 
\sphinxAtStartPar
SolidWorks Known to a few of the Authors from previous lives.

\item {} 
\sphinxAtStartPar
Autodesk’s Fusion/360 popular (indeed basis for LowSpec). Autodesk is not as freely accessible to the community as before.

\item {} 
\sphinxAtStartPar
TinkerCAD modify STL files, capture basic designs.

\item {} 
\sphinxAtStartPar
Cura convert STL into gcode

\item {} 
\sphinxAtStartPar
KiCAD for the electrical layout. The Power Supply Board was used.

\item {} 
\sphinxAtStartPar
Octoprint, used to readily transfer gcode to the 3D printer.

\end{enumerate}

\chapter{Electronics}
\label{\detokenize{electronics:electronics}}\label{\detokenize{electronics::doc}}
\sphinxAtStartPar
Clarke Yeager, used KiCad \sphinxcite{references:kicad-1} to create the schematic and layout for
several Printed Circuit Boards, emailed to China, made \textendash{} with silk
screen overlays and returned. The total cost was around 0.50USD per
board, shipping was more than the costs of the boards. This package
was emailed to Tony Rodda in England where he originated his own
order. Shipping time in Europe was less than for Clarke in the US.

\begin{figure}[htbp]
\centering
\capstart

\noindent\sphinxincludegraphics{{KiCadBoards1}.jpeg}
\caption{\sphinxhref{https://KiCad.org}{KiCad} boards. A completed high\sphinxhyphen{}voltage board, without the Arduino BLE Sense attached to bottom, shown over a top and bottom image for the board. To the side is a smaller board for stepper controllers.}\label{\detokenize{electronics:id2}}\end{figure}

\sphinxAtStartPar
TODO Add Schematics

\chapter{Arduino Chips}
\label{\detokenize{arduino:arduino-chips}}\label{\detokenize{arduino::doc}}
\sphinxAtStartPar
Follow the instructions:

\sphinxAtStartPar
\sphinxhref{https://wiki.seeedstudio.com/Seeeduino-XIAO/}{Seeeduino XIAO}

\sphinxAtStartPar
Arduino chips come in several flavors. Here we are using Arm \sphinxhyphen{}Core \index{Arm@\spxentry{Arm}}Arm processors.

\sphinxAtStartPar
Download the Arduino IDE (here 1.8.15)

\sphinxAtStartPar
Under \sphinxstylestrong{File \sphinxhyphen{}\textgreater{} Preferences}

\sphinxAtStartPar
Into the \sphinxstylestrong{Additional Boards Manager URLs} enter:

\sphinxAtStartPar
“\sphinxurl{https://files.seeedstudio.com/arduino/package\_seeeduino\_boards\_index.json}”

\sphinxAtStartPar
\sphinxstylestrong{Tools \sphinxhyphen{}\textgreater{} Board \sphinxhyphen{}\textgreater{} Boards Manager}

\sphinxAtStartPar
Search/select \sphinxstylestrong{Seeed SAMD Boards} (see that it includes
Seeeduino XAIO M0, and install it. (here 1.21.1) Takes a beat.

\sphinxAtStartPar
The real trick is to start with the raw IDE and add the \sphinxstylestrong{Blink}
program. This shows the ‘loop’ is closed with respect to development.

\section{Pin Outs}
\label{\detokenize{arduino:pin-outs}}
\begin{sphinxVerbatim}[commandchars=\\\{\},numbers=left,firstnumber=1,stepnumber=1]
Pin Funcion Type Description
1  D13          Digital GPIO
2  +3V3 Power Out Internally generated power output to external devices
3  AREF         Analog           Analog Reference; can be used as GPIO
4  A0/DAC0      Analog ADC in/DAC out; can be used as GPIO
5  A1           Analog ADC in; can be used as GPIO
6  A2           Analog ADC in; can be used as GPIO
7  A3           Analog ADC in; can be used as GPIO
8  A4/SDA       Analog ADC in; I2C SDA; Can be used as GPIO (*)
9  A5/SCL       Analog ADC in; I2C SCL; Can be used as GPIO(*)
10 A6           Analog ADC in; can be used as GPIO
11 A7           Analog ADC in; can be used as GPIO
12 VUSB Normally NC;
13 RST          Digital In Active low reset input (duplicate of pin 18)
14 GND Power Power Ground
15 VIN Power In Vin Power input
16 TX           Digital USART TX; can be used as GPIO
17 RX           Digital USART RX; can be used as GPIO
18 RST          Digital Active low reset input (duplicate of pin 13)
19 GND Power Power Ground
20 D2           Digital GPIO
21 D3/PWM       Digital GPIO; can be used as PWM
22 D4           Digital GPIO
23 D5/PWM       Digital GPIO; can be used as PWM
24 D6/PWM       Digital GPIO; can be used as PWM
25 D7           Digital GPIO
26 D8           Digital GPIO
27 D9/PWM       Digital GPIO; can be used as PWM
28 D10/PWM      Digital GPIO; can be used as PWM
29 D11/MOSI     Digital SPI MOSI; can be used as GPIO
30 D12/MISO     Digital SPI MISO; can be used as GPIO
\end{sphinxVerbatim}
\begin{description}
\item[{Note: (12)can be connected to VUSB pin of the USB connector by shorting}] \leavevmode
\sphinxAtStartPar
a jumper Power In/Out

\end{description}
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

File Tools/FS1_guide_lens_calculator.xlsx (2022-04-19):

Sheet: Sheet1
FS1 Guide lens and guide field of view calculator
Jerry Foote 1/2/2022
Guide Camera: | QHY5III174
 | Theoretical | Actual | Notes
Illuminated slit width (mm)= | 10 | 10 | This is near the maximum width of the usable image on the OVIO slit disk
Illuminated slit height (mm)= | 7 | 7 | This is near the maximum height of the usable image on the OVIO slit disk
Slit Lens focal length (mm)= | 65 | 50 | 50 mm is the shortest focal length slit lens that doesn't vignet the incoming beam
Width of guide chip (mm)= | 11.25 | 11.25 | These values come from the guide camera table
Height of guide chip (mm)= | 7.03 | 7.03 | These values come from the guide camera table
Desired slit magnification= | 1.12 | 1.12
Camera lens focal length (mm)= | 73.12 | 45.00 | This is the focal length of the guide lens that allows the guide camera to be fully illuminated. However make sure that the guide camera has sufficient back focus to bring the image into focus.
Actual magnification= | 1.12 | 0.90
Slit width (microns)= | 20 | 20
Guide camera pixel width(microns)= | 5.86 | 5.86 | These values come from the guide camera table
number of pixels covered by slit= | 3.84 | 3.07
Telescope Focal length (mm)= | 1422 | 1422
Horizontal FOV (arc minutes)= | 24.18 | 19.34
Vertical FOV (arc Minutes)= | 16.92 | 13.54

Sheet: Guide camera table
Camera | H Size | V Size | P Size
Lodestar Pro 2 | 6.47 | 4.81 | 8.5
Lodestar X2 | 6.45 | 4.75 | 8.3
StarShoot | 6.6 | 5.32 | 5.2
QHY5III174 | 11.25 | 7.03 | 5.86
QHY5III178 | 7.37 | 4.92 | 2.4
QHY5III290M | 5.57 | 3.13 | 2.9
QHY5III485C | 11.21 | 6.32 | 2.9

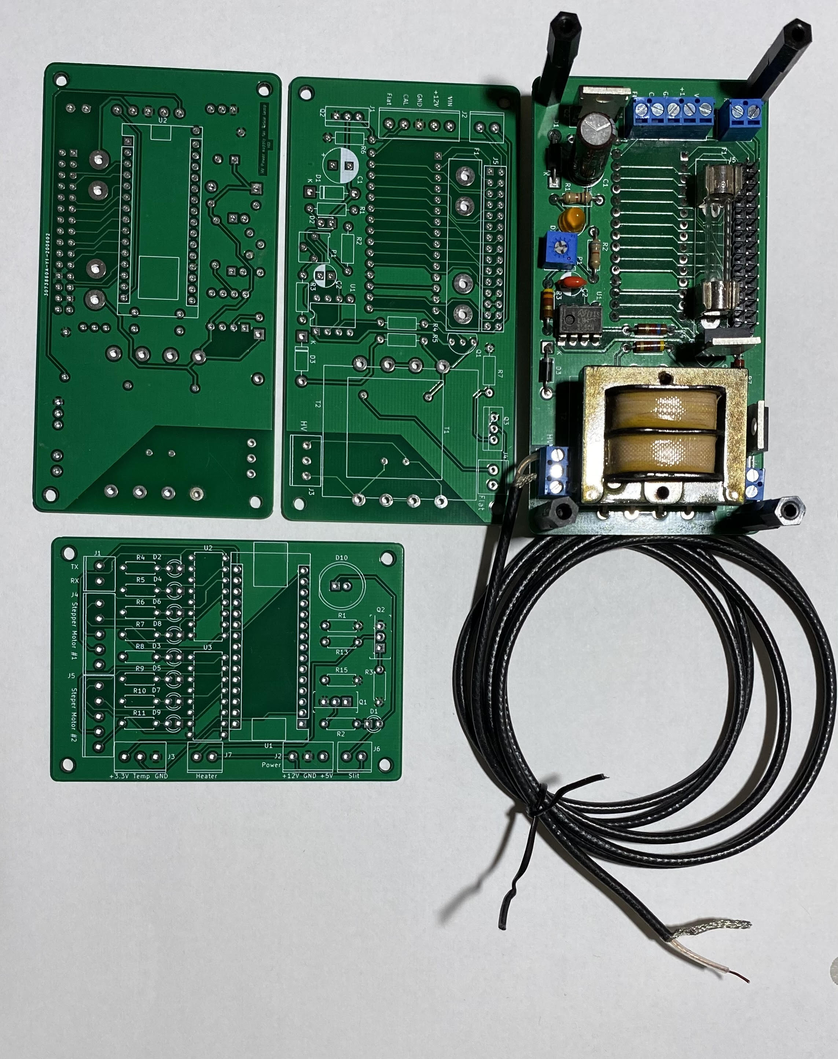
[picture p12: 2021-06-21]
docs/build/html/_images/KiCadBoards1.jpeg

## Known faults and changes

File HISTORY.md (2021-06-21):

HISTORY
-------

V0.1  17 June 2021 tagged the work-in-progress release.
      Massive upload of documentation/notes. Upload of the
      python code for Bokeh interface to the project.

      TODO: Flesh-out the total Postmaster structure.
            Add the C++/Arduino side of the code.

V0.0  8 April 2021 Initial creation with small updates as placeholder.

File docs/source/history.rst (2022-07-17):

History
=======

During the AAVSO meeting in Flagstaff, AZ. 16-17 November 2018 -- Cary
Chleborad, Eric Dose, Wayne Green, Michael Lundquist, Tony Rodda
Forrest Sims took an interest into Tony's 3D printing of a
spectrograph.

The Sacramento Mountian Spectroscopy Workshop II, held in Las Curzes
NM on 22-24 February, 2019. At the meeting, Jerry Foote, Wayne Green,
Michael Lundquist, Forrest Sims, Tom Smith agreed it was time to print
the Lowspec improve things.  Clarke Yeager and Greg Jones joined
later.

To this end, the FlexSpec-1 was born. 

We started with first principles and have redesigned several aspects
of current small spectroscope offerings. We are using the
counterposing aspects of a aluminum/steel chassis to fix flexure,
opacity and thermal expansion. 3D printing has proved viable for the
comparatively tiny components supporting the optics within this
chassis. Our software deployment does not require end-user
installation of any programs.  Operations are possible from anywhere
in netdom. We are rather proud of our guide improvements, Fraunhofer
baffle, focusable collimator, Kzin ring calibration and general
automation.

A complete discussion of the work may be found in the Proceedings
of the Society for Astronomical Sciences, 2020, 2021 and 2022.
`Publications <https://socastrosci.org/publications/>`_ and
`Videos <https://socastrosci.org/videos/>`_ .

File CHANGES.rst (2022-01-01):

CHANGES
=======

A terse/condensed version of this file will appear later in development.

V 0.0.1: (newest on top)
------------------------

2021-07-23T12:24:02-0600
   - Code/SBC/server.py to handle switches, trap exit, better reporting.
   - Code/FlexSpec/UserInterface/Guider.py to consistent with other JSON 
     strings.
   - Code/FlexSpec/UserInterface/FlexSpec handle clean up better

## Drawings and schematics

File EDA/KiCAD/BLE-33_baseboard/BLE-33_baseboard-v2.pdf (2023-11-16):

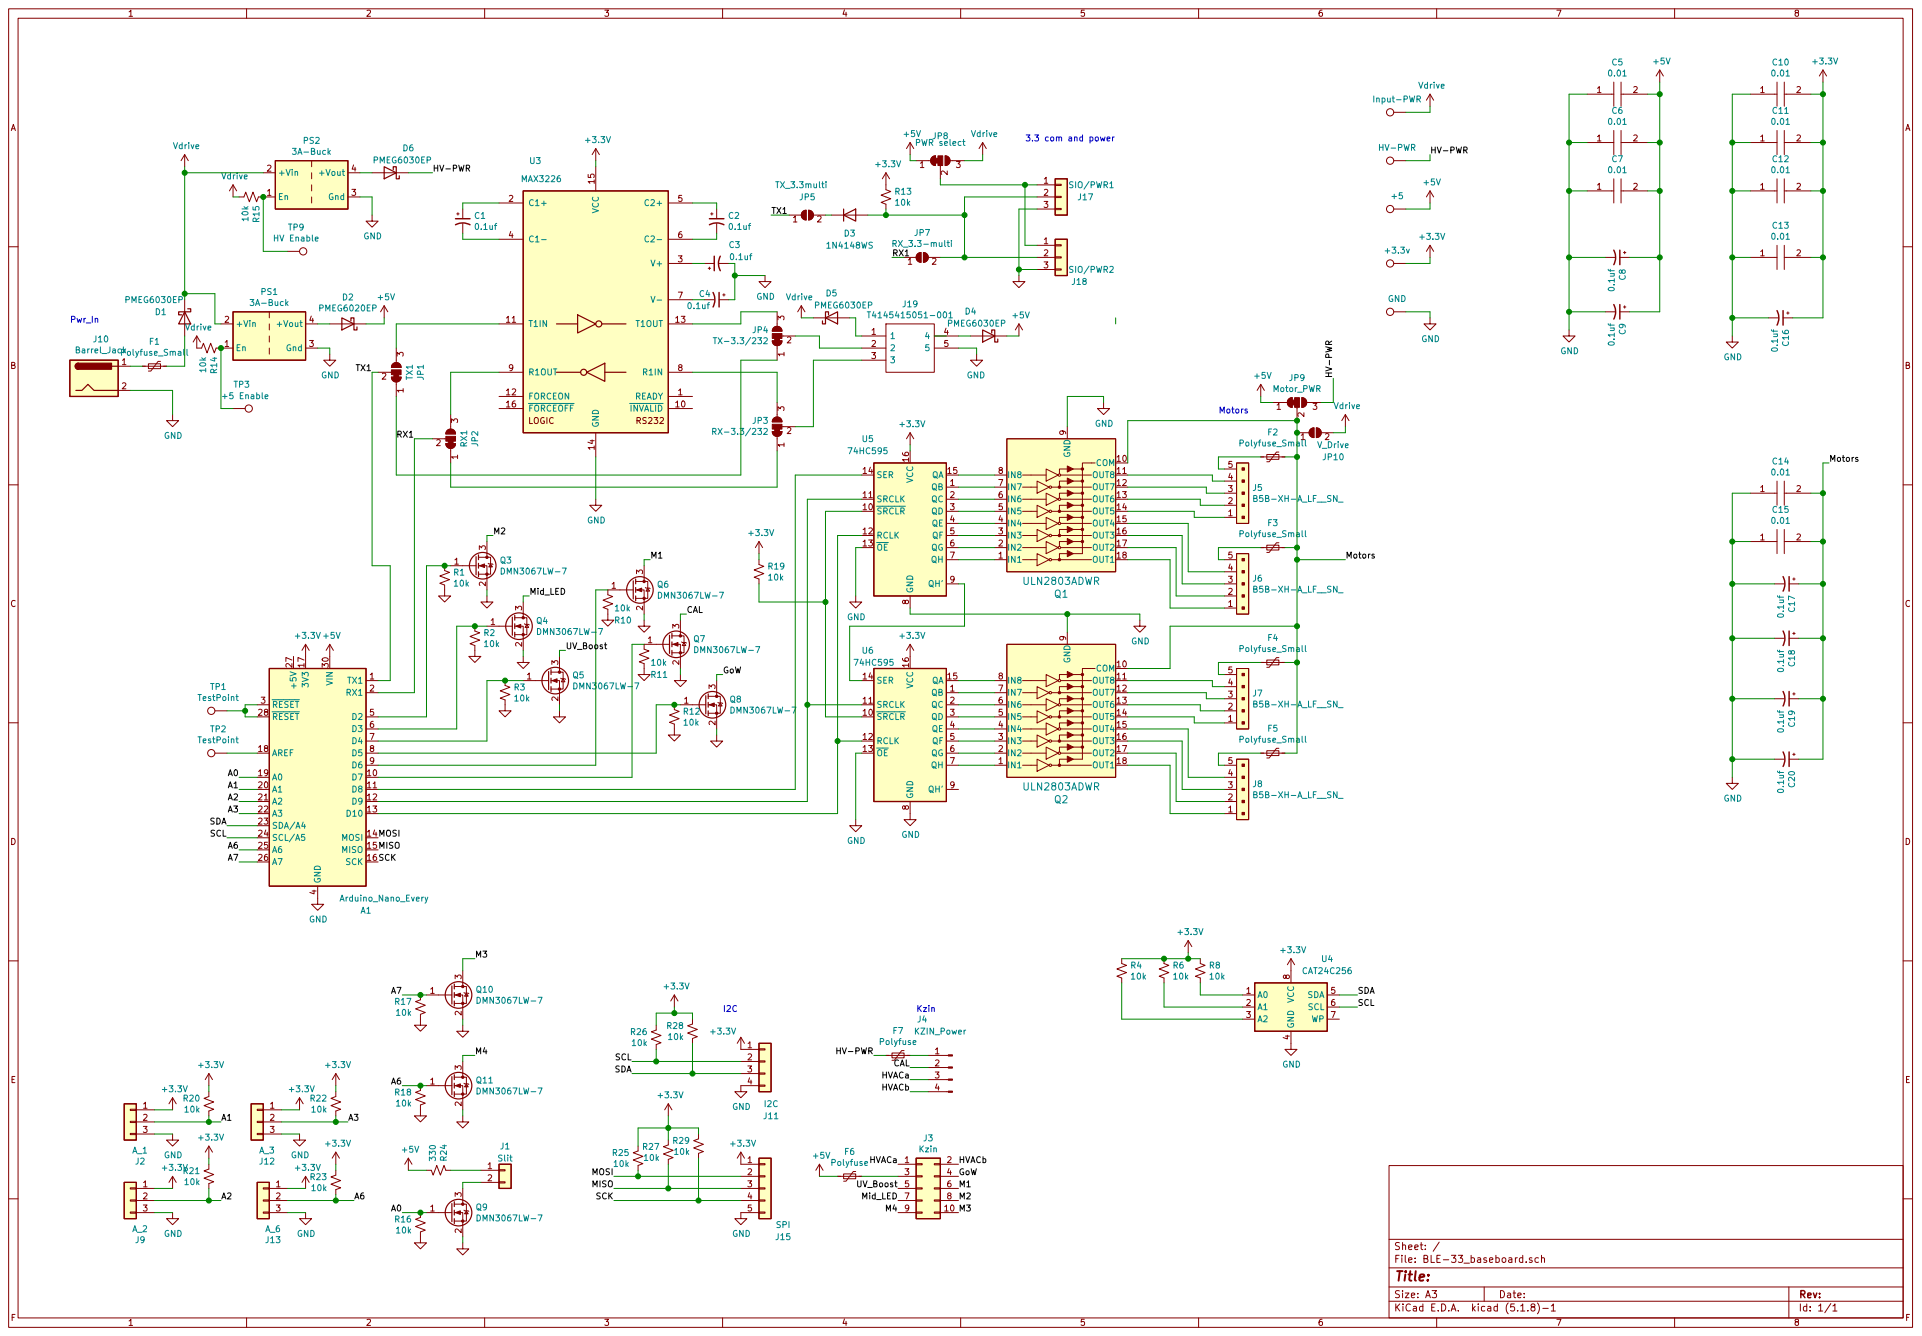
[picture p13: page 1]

2 3 Q10 DMN3067LW-7 TX1 1 D7 10 D8 11 D9 12 D10 13 MOSI 14 MISO 15 SCK 16 3V3 17 AREF 18 A0 19 RX1 2 A1 20 A2 21 A3 22 SDA/A4 23 SCL/A5 24 A6 25 A7 26 +5V 27 RESET 28 RESET 3 VIN 30 GND

4 SDA 5 SCL 6 WP 7 VCC

File: BLE-33_baseboard.sch Sheet: /

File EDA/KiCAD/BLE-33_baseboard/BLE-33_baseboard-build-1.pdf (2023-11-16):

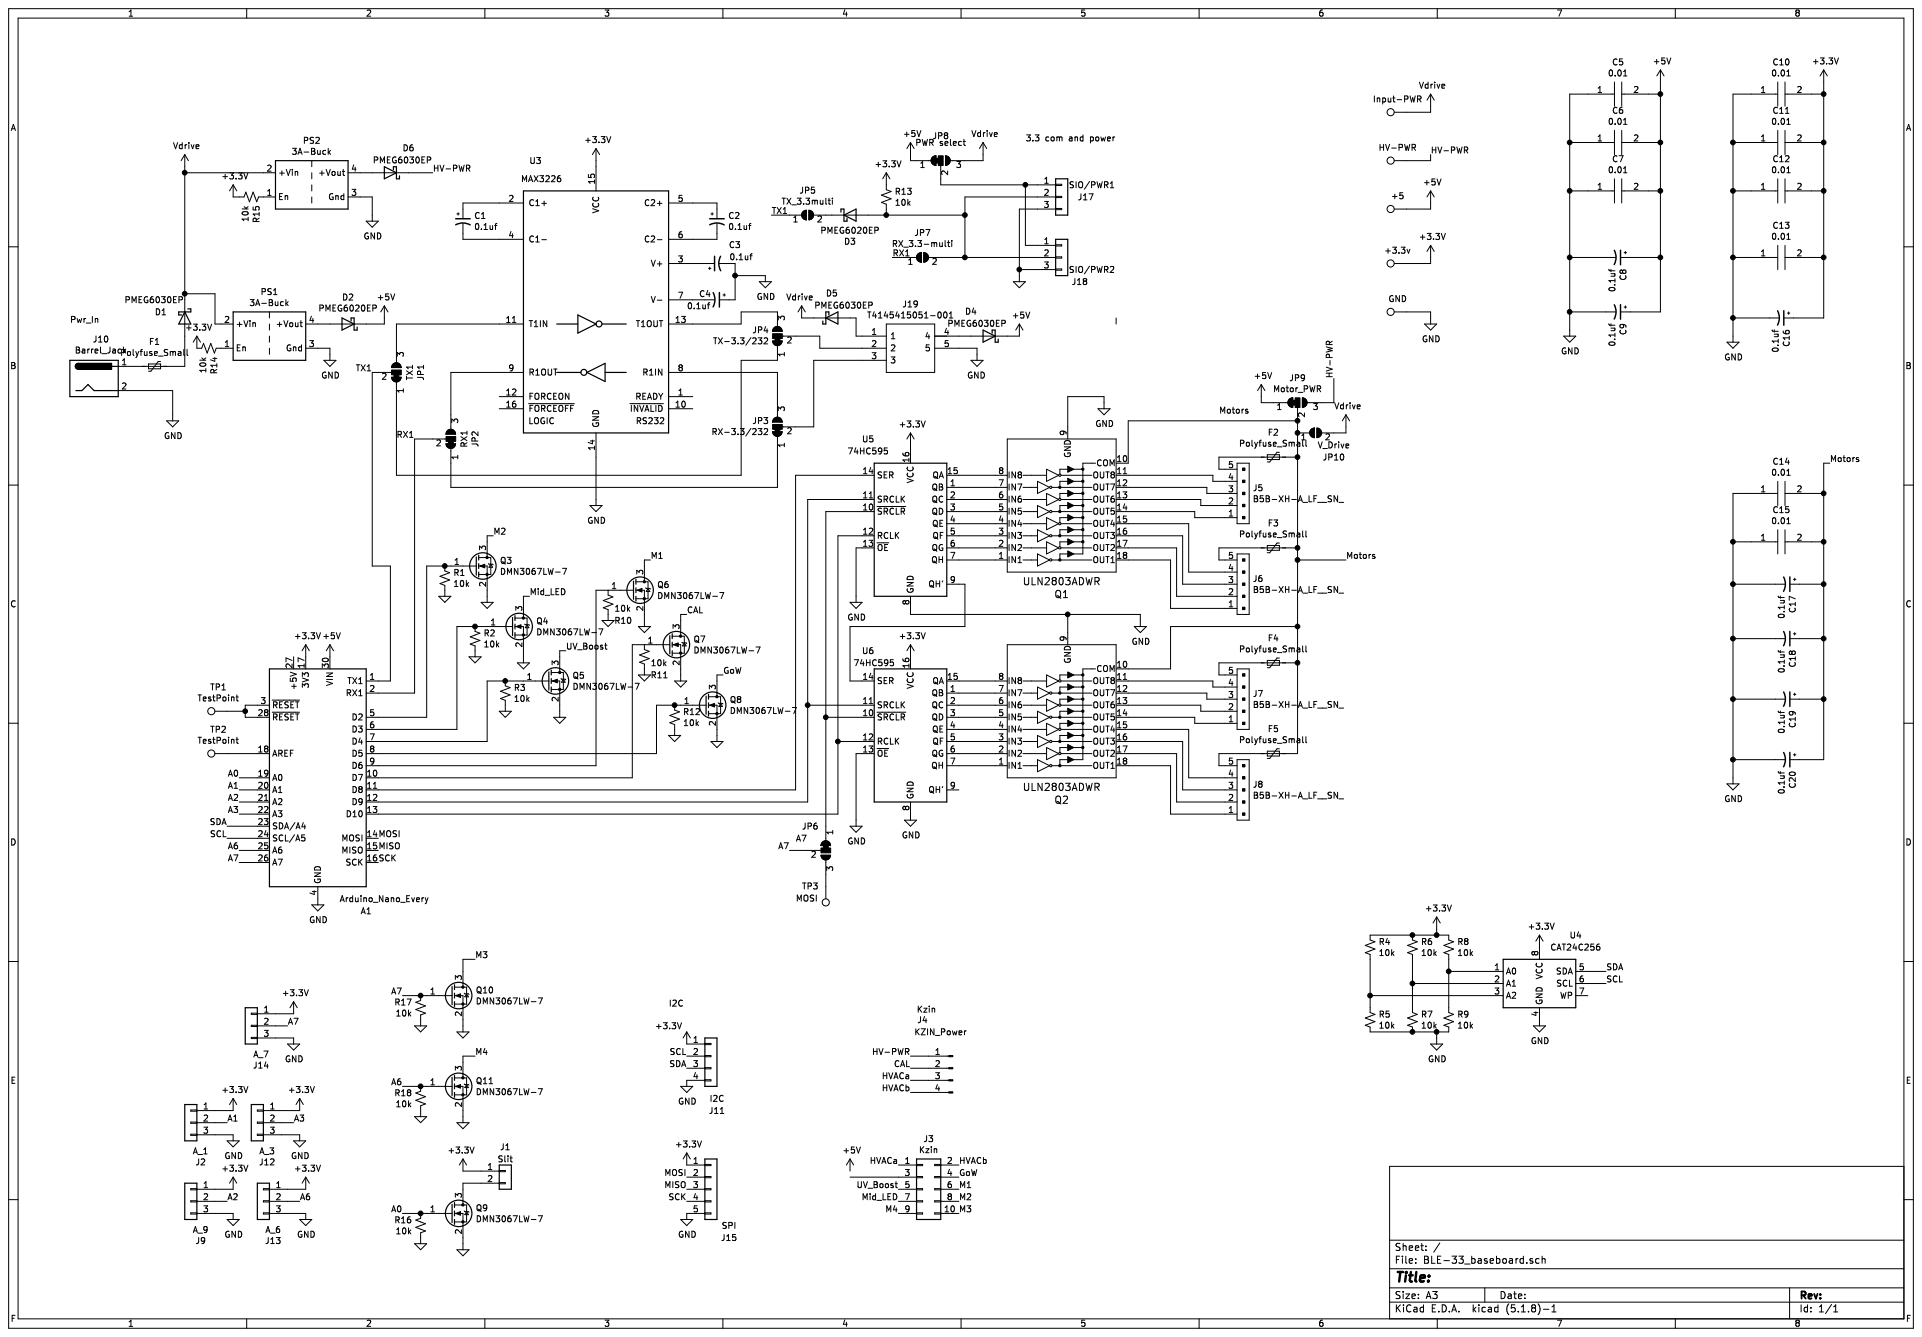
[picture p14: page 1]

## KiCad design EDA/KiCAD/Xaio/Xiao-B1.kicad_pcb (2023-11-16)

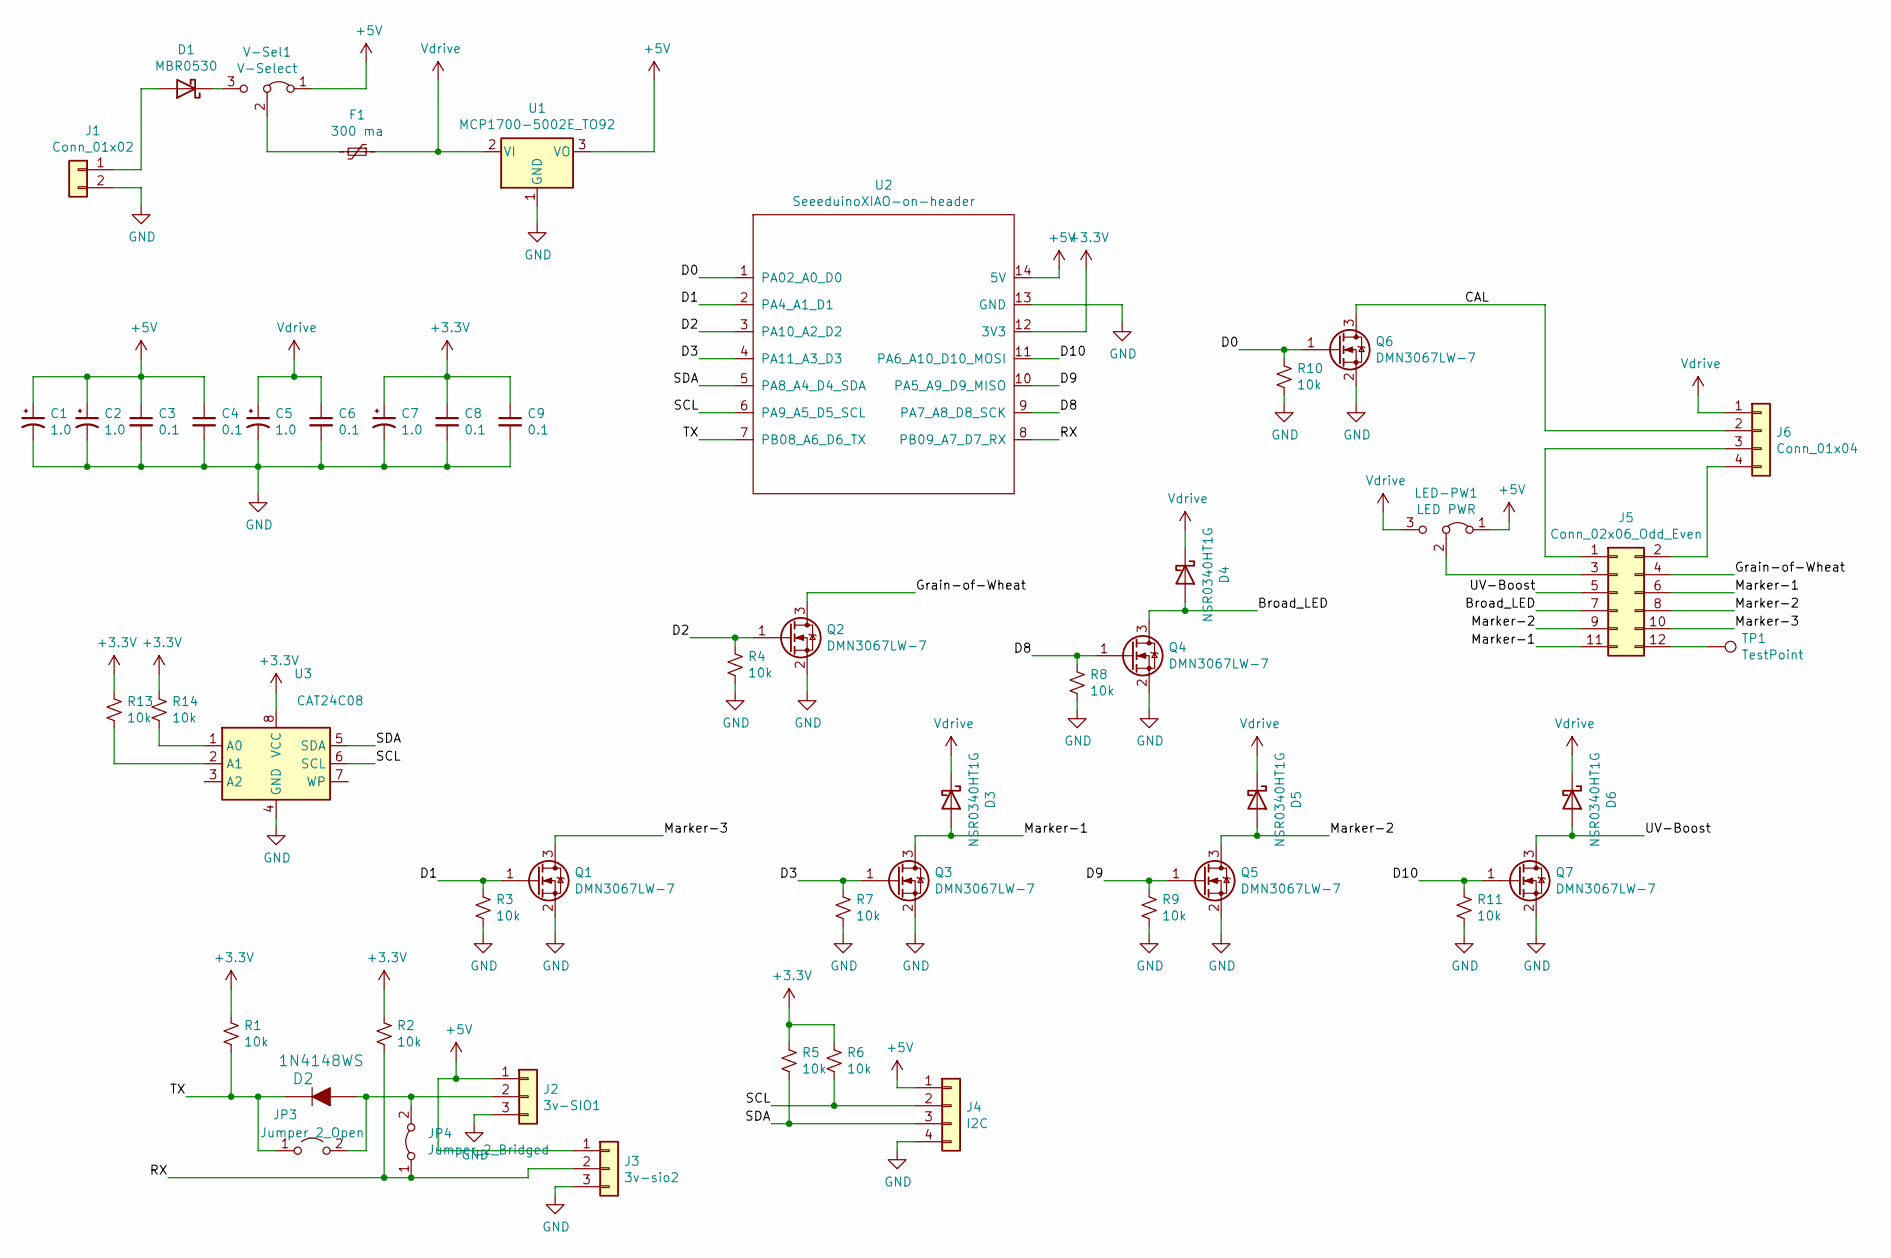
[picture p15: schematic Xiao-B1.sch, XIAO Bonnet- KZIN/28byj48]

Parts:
C1, C2, C5, C7: 1.0; C_0805_2012Metric_Pad1.18x1.45mm_HandSolder; MPN CL21A225KAFNNNE; JLCPCB C87994
C3, C4, C6, C8, C9: 0.1; C_0402_1005Metric_Pad0.74x0.62mm_HandSolder; MPN 0402X104K250CT; JLCPCB C237172
D1: MBR0530; D_SOD-123; MPN MBR0530; JLCPCB C475718
D2: 1N4148WS; SOD-323F; MPN 1N4148WS; Digi-Key_PN 1N4148WSFSCT-ND
D3, D4, D5, D6: NSR0340HT1G; D_SOD-323; MPN NSR0340HT1G; JLCPCB C90392
F1: 300 ma; Fuse_0805_2012Metric; MPN 0805L010/24YR; JLCPCB C207019
J1: Conn_01x02; PinHeader_1x02_P2.54mm_Vertical
J2: 3v-SIO1; Hirose_DF13-03P-1.25DSA_1x03_P1.25mm_Vertical; MPN 0530470310; Digi-Key_PN WM1732-ND
J3: 3v-sio2; Hirose_DF13-03P-1.25DSA_1x03_P1.25mm_Vertical; MPN 0530470310; Digi-Key_PN WM1732-ND
J4: I2C; Hirose_DF13-04P-1.25DSA_1x04_P1.25mm_Vertical; MPN 0530470410; Digi-Key_PN WM1733-ND
J5: Conn_02x06_Odd_Even; PinHeader_2x06_P2.54mm_Vertical; Mouser_PN 437-8038701020001101
J6: Conn_01x04; PinHeader_1x04_P2.54mm_Vertical
JP3: Jumper_2_Open; SolderJumper-2_P1.3mm_Open_Pad1.0x1.5mm
JP4: Jumper_2_Bridged; SolderJumper-2_P1.3mm_Bridged_Pad1.0x1.5mm
LED-PW1: LED PWR; SolderJumper-3_P1.3mm_Bridged12_Pad1.0x1.5mm_NumberLabels
Q1, Q2, Q3, Q4, Q5, Q6, Q7: DMN3067LW-7; SOT-323_SC-70_Handsoldering; MPN DMN3067LW-7; JLCPCB C212325
R1, R2, R3, R4, R5, R6, R7, R8, R9, R10, R11, R13, R14: 10k; R_0603_1608Metric_Pad0.98x0.95mm_HandSolder; MPN RC0603FR-0710KL; JLCPCB C98220
TP1: TestPoint; TestPoint_THTPad_1.0x1.0mm_Drill0.5mm
U1: MCP1700-5002E_TO92; TO-92_Inline
U2: SeeeduinoXIAO-on-header; Xiao-on-Header
U3: CAT24C08; TSSOP-8_4.4x3mm_P0.65mm; MPN CAT24C08YI-GT3; JLCPCB C193225
V-Sel1: V-Select; SolderJumper-3_P1.3mm_Bridged12_Pad1.0x1.5mm_NumberLabels

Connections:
+3V3: C7.1, C8.1, C9.1, R1.1, R2.1, R5.1, R6.1, R13.1, R14.1, U2.12 (3V3), U3.8 (VCC)
+5V: C1.1, C2.1, C3.1, C4.1, J2.1, J3.1, J4.1, LED-PW1.1 (A), U1.3 (VO), U2.14 (5V), V-Sel1.1 (A)
/Broad_LED: D4.2 (A), J5.7, Q4.3 (D)
/CAL: J6.2, Q6.3 (D)
/D0: Q6.1 (G), R10.1, U2.1 (PA02_A0_D0)
/D1: Q1.1 (G), R3.1, U2.2 (PA4_A1_D1)
/D2: Q2.1 (G), R4.1, U2.3 (PA10_A2_D2)
/D3: Q3.1 (G), R7.1, U2.4 (PA11_A3_D3)
/D8: Q4.1 (G), R8.1, U2.9 (PA7_A8_D8_SCK)
/D9: Q5.1 (G), R9.1, U2.10 (PA5_A9_D9_MISO)
/D10: Q7.1 (G), R11.1, U2.11 (PA6_A10_D10_MOSI)
/Grain-of-Wheat: J5.4, Q2.3 (D)
/Marker-1: D3.2 (A), J5.6, J5.11, Q3.3 (D)
/Marker-2: D5.2 (A), J5.8, J5.9, Q5.3 (D)
/Marker-3: J5.10, Q1.3 (D)
/RX: J3.2, JP4.1 (A), R2.2, U2.8 (PB09_A7_D7_RX)
/SCL: J4.2, R6.2, U2.6 (PA9_A5_D5_SCL), U3.6 (SCL)
/SDA: J4.3, R5.2, U2.5 (PA8_A4_D4_SDA), U3.5 (SDA)
/TX: D2.K, JP3.1 (A), R1.2, U2.7 (PB08_A6_D6_TX)
/UV-Boost: D6.2 (A), J5.5, Q7.3 (D)
GND: C1.2, C2.2, C3.2, C4.2, C5.2, C6.2, C7.2, C8.2, C9.2, J1.2, J2.3, J3.3, J4.4, Q1.2 (S), Q2.2 (S), Q3.2 (S), Q4.2 (S), Q5.2 (S), Q6.2 (S), Q7.2 (S), R3.2, R4.2, R7.2, R8.2, R9.2, R10.2, R11.2, U1.1 (GND), U2.13 (GND), U3.4 (GND)
unnamed: D1.1 (K), V-Sel1.3 (B)
unnamed: D1.2 (A), J1.1
unnamed: D2.A, J2.2, JP3.2 (B), JP4.2 (B)
unnamed: F1.2, V-Sel1.2 (C)
unnamed: J5.1, J6.3
unnamed: J5.2, J6.4
unnamed: J5.3, LED-PW1.2 (C)
unnamed: J5.12, TP1.1
unnamed: R13.2, U3.2 (A1)
unnamed: R14.2, U3.1 (A0)
Vdrive: C5.1, C6.1, D3.1 (K), D4.1 (K), D5.1 (K), D6.1 (K), F1.1, J6.1, LED-PW1.3 (B), U1.2 (VI)

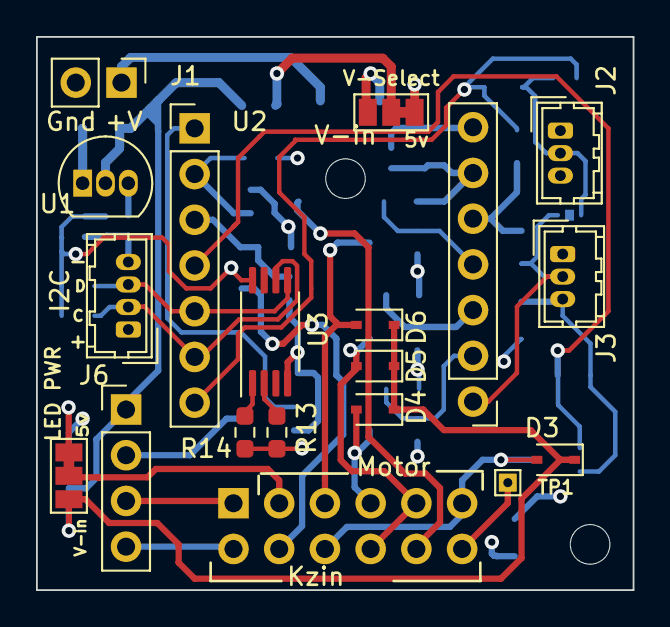
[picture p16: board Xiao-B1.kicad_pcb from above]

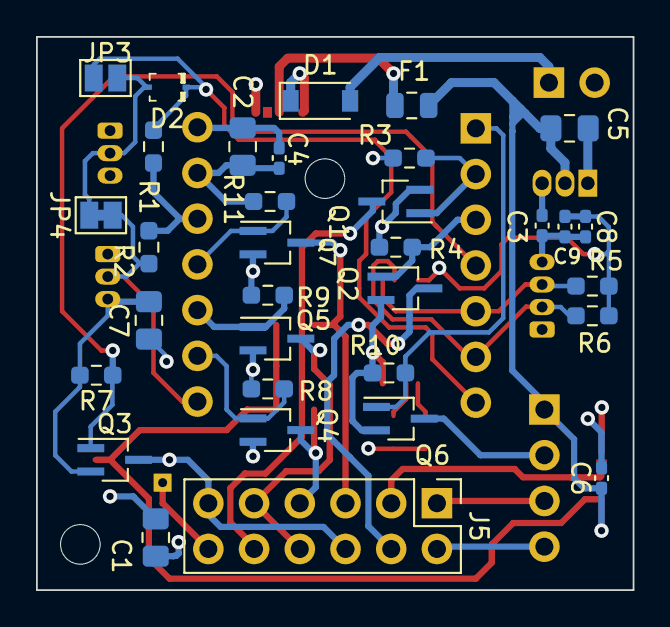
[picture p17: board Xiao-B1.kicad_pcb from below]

Board: 4 copper layers, 33.1 x 30.7 mm, 52 parts (33 on the bottom side), 32 nets.

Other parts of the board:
M: MountingHole_2.2mm_M2
M#2: MountingHole_2.2mm_M2

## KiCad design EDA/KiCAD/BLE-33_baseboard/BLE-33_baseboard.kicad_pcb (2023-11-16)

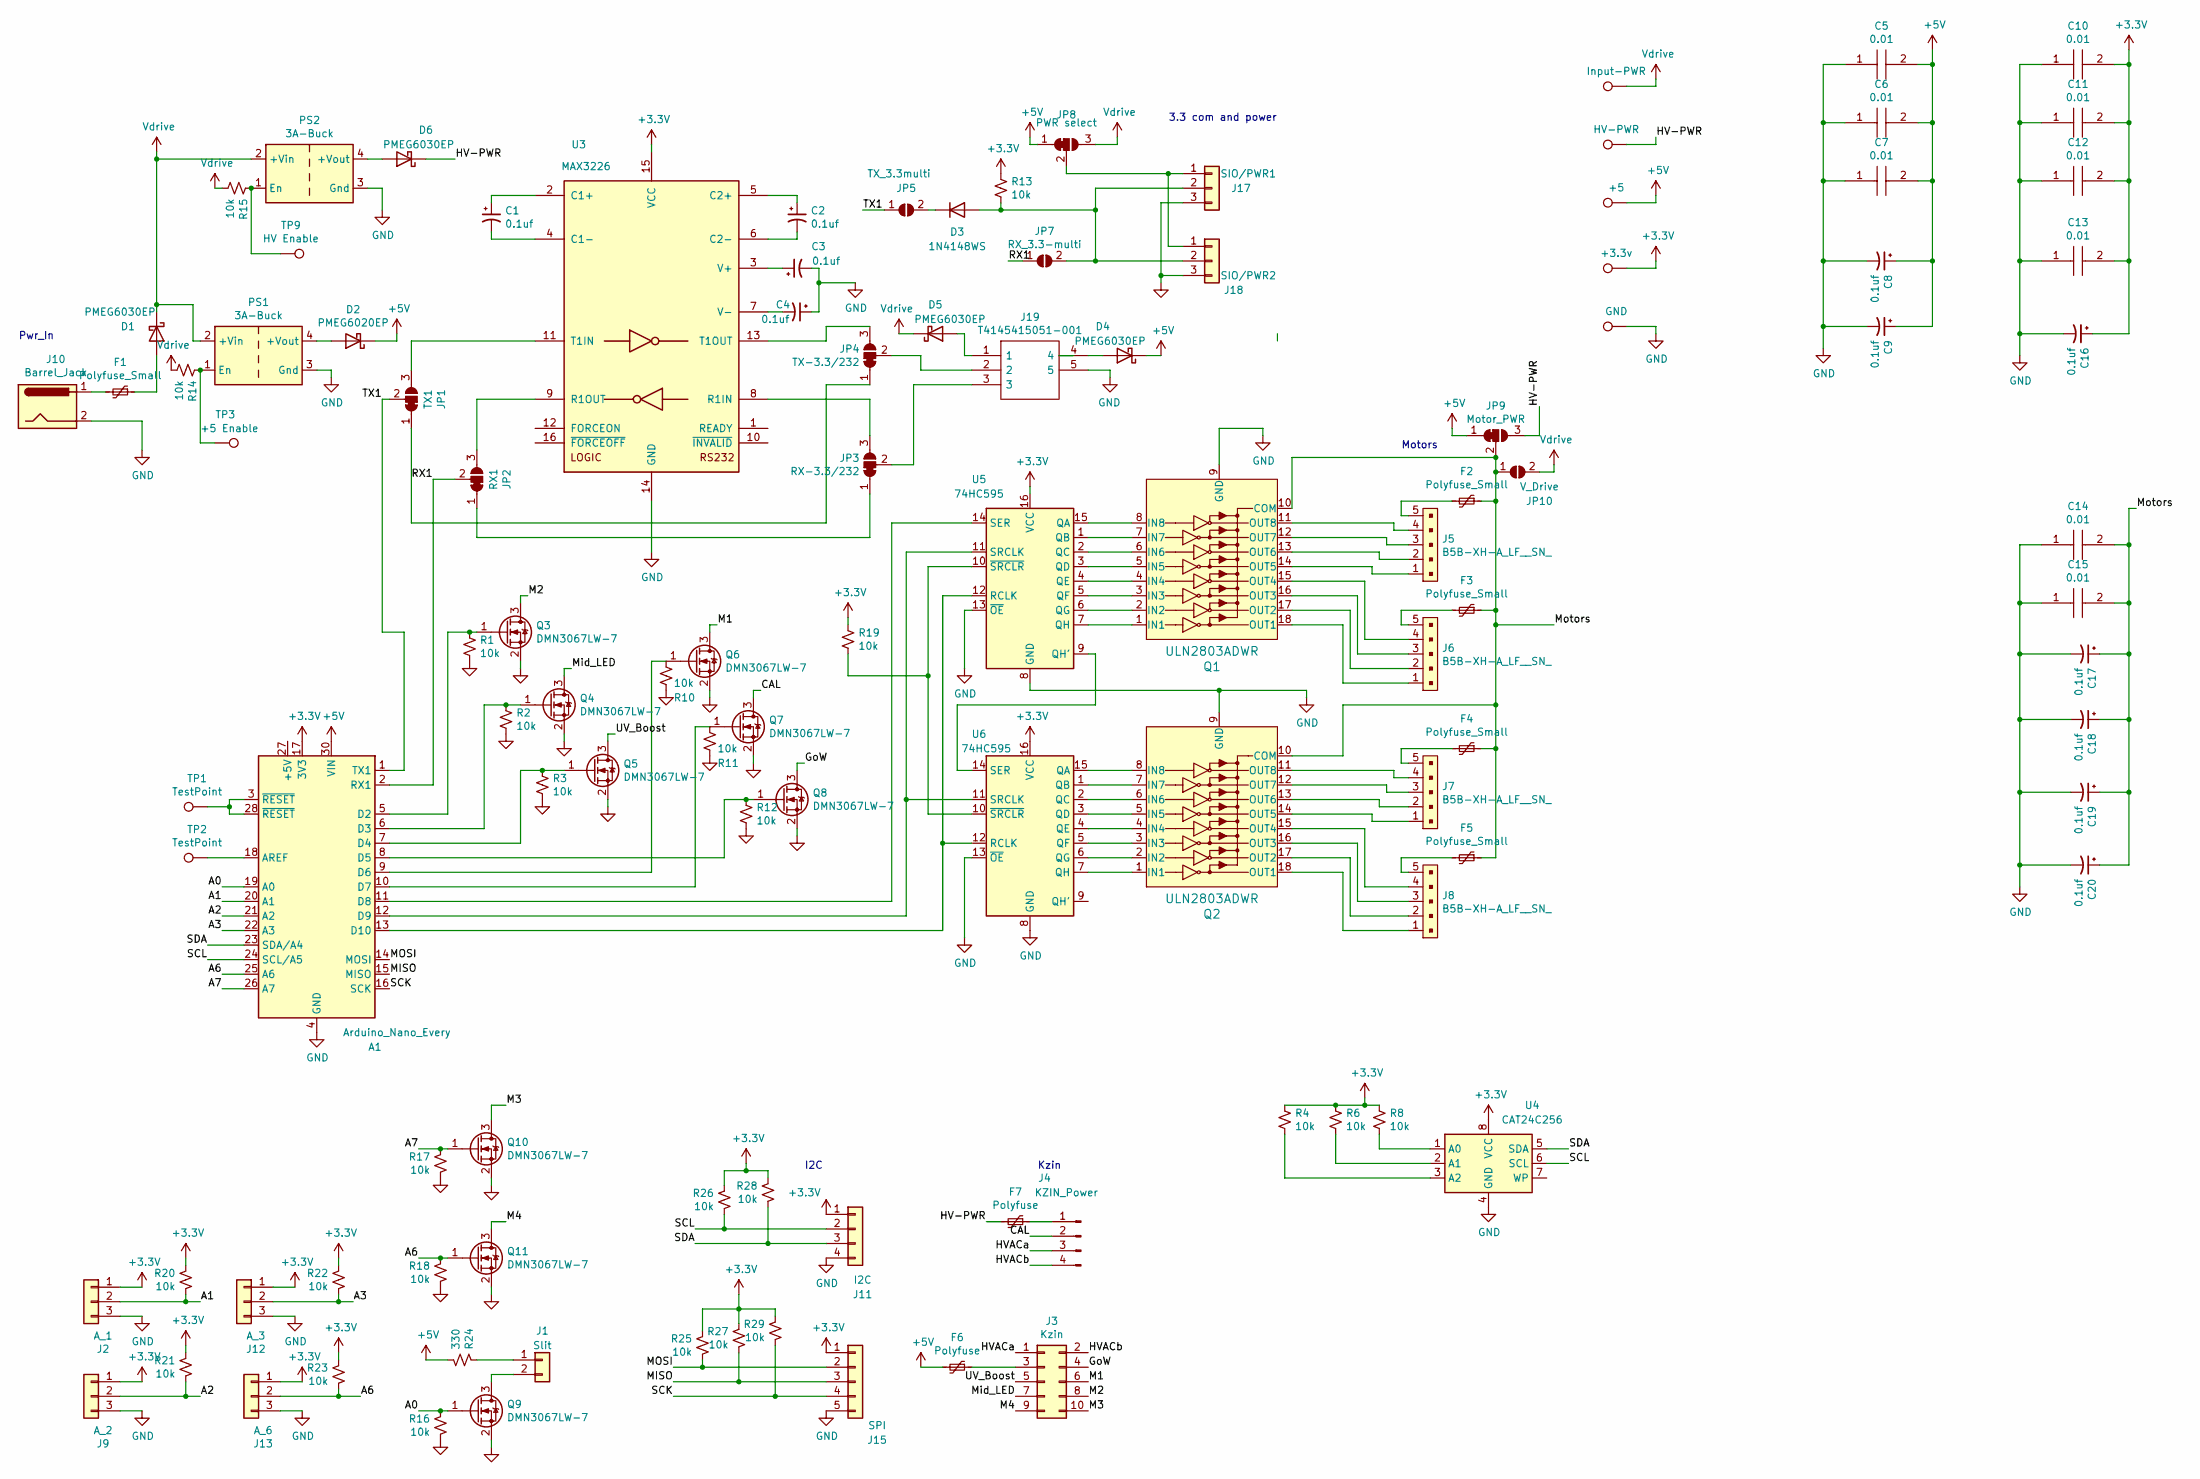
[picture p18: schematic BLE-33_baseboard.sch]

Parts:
A1: Arduino_Nano_Every; Arduino_Nano
C1, C2, C3, C4: 0.1uf; C_0805_2012Metric; MPN TAJR104M035RNJ; Digi-Key_PN 478-11592-1-ND
C5, C6, C7, C10, C11, C12, C13, C14, C15: 0.01; CAPC1608X90N; Manufacturer_Part_Number CGA3E2X7R1H103K080AA; Mouser Part Number 810-CGA3E2X7R1H103K
C8, C9, C16, C17, C18, C19, C20: 0.1uf; C_0805_2012Metric; MPN TAJR104M035RNJ; Digi-Key 478-11592-1-ND
D1: PMEG6030EP; D_SOD-128
D2: PMEG6020EP; D_SOD-128; MPN PMEG6030EP/8X; Digi-Key 1727-7646-1-ND
D3: 1N4148WS; D_SOD-323
D4, D6: PMEG6030EP; D_SOD-128; MPN PMEG6030EP/8X; Digi-Key 1727-7646-1-ND
D5: PMEG6030EP; D_SOD-128; MPN PMEG6030EP/8X; Digi-Key_PN 1727-7646-1-ND
F1: Polyfuse_Small; Fuse_1206_3216Metric; MPN 0ZCJ0075AF2E; Digi-Key 507-1805-1-ND
F2, F3, F4, F5: Polyfuse_Small; Fuse_0805_2012Metric; MPN 0805L020YR; Digi-Key F2770CT-ND
F6, F7: Polyfuse; Fuse_0805_2012Metric; MPN 0805L020YR; Digi-Key F2770CT-ND
J1: Slit; Hirose_DF13-02P-1.25DSA_1x02_P1.25mm_Vertical; MPN 0530470210; Digi-Key WM1731-ND
J2: A_1; Hirose_DF13-03P-1.25DSA_1x03_P1.25mm_Vertical; Digi-Key WM1732-ND
J3: Kzin; PinHeader_2x05_P2.54mm_Horizontal; Digi-Key 10129382-910004BLF-ND
J4: KZIN_Power; PinHeader_1x04_P2.54mm_Horizontal; Digi-Key WM4302-ND
J5, J6, J7, J8: B5B-XH-A_LF__SN_; JST_XH_B5B-XH-AM_1x05_P2.50mm_Vertical; MPN B5B-XH-AM(LF)(SN); Digi-Key 455-2239-ND
J9: A_2; Hirose_DF13-03P-1.25DSA_1x03_P1.25mm_Vertical; Digi-Key WM1732-ND
J10: Barrel_Jack; BarrelJack_CUI_PJ-063AH_Horizontal_CircularHoles; MPN PJ-063AH; Digi-Key CP-063AH-ND
J11: I2C; Molex_PicoBlade_53047-0410_1x04_P1.25mm_Vertical; Digi-Key WM1733-ND
J12: A_3; Hirose_DF13-03P-1.25DSA_1x03_P1.25mm_Vertical; Digi-Key WM1732-ND
J13: A_6; Hirose_DF13-03P-1.25DSA_1x03_P1.25mm_Vertical; Digi-Key WM1732-ND
J15: SPI; Molex_PicoBlade_53047-0510_1x05_P1.25mm_Vertical; Digi-Key WM1734-ND
J17: SIO/PWR1; Hirose_DF13-03P-1.25DSA_1x03_P1.25mm_Vertical; Digi-Key WM1732-ND
J18: SIO/PWR2; Hirose_DF13-03P-1.25DSA_1x03_P1.25mm_Vertical; Digi-Key WM1732-ND
J19: T4145415051-001; T4145415051001; Manufacturer_Part_Number T4145415051-001; Mouser Part Number 571-T4145415051-001
JP1: TX1; SolderJumper-3_P1.3mm_Bridged12_RoundedPad1.0x1.5mm_NumberL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
JP2: RX1; SolderJumper-3_P1.3mm_Bridged12_RoundedPad1.0x1.5mm_NumberL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
JP3: RX-3.3/232; SolderJumper-3_P1.3mm_Bridged12_RoundedPad1.0x1.5mm_NumberL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
JP4: TX-3.3/232; SolderJumper-3_P1.3mm_Bridged12_RoundedPad1.0x1.5mm_NumberL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
JP5: TX_3.3multi; SolderJumper-2_P1.3mm_Open_Pad1.0x1.5mm
JP7: RX_3.3-multi; SolderJumper-2_P1.3mm_Open_Pad1.0x1.5mm
JP8: PWR select; SolderJumper-3_P1.3mm_Bridged12_RoundedPad1.0x1.5mm_NumberL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
JP9: Motor_PWR; SolderJumper-3_P1.3mm_Bridged12_RoundedPad1.0x1.5mm_NumberL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
JP10: V_Drive; SolderJumper-2_P1.3mm_Open_Pad1.0x1.5mm
PS1, PS2: 3A-Buck; Converter_DCDC_3A-Buck
Q1, Q2: ULN2803ADWR; SOIC-18_W7.5mm; MPN ULN2803ADWR; Digi-Key 296-15777-1-ND
Q3, Q4, Q5, Q6, Q7, Q8, Q9, Q10, Q11: DMN3067LW-7; SOT-323_SC-70; MPN DMN3067LW-7; Digi-Key DMN3067LW-7DICT-ND
R1, R2, R3, R4, R6, R8, R10, R11, R12, R13, R14, R16, R17, R18, R19, R20, R21, R22, R23, R25, R26, R27, R28, R29: 10k; R_0805_2012Metric; MPN SR0805JR-0710KL; Digi-Key 13-SR0805JR-0710KLCT-ND
R15: 10k; R_0805_2012Metric; MPN SR0805JR-0710KL; Digi-Key_PN 13-SR0805JR-0710KLCT-ND
R24: 330; R_1206_3216Metric
TP1, TP2: TestPoint; TestPoint_THTPad_D1.0mm_Drill0.5mm
TP3: +5 Enable; TestPoint_THTPad_D1.0mm_Drill0.5mm
TP4: HV-PWR; TestPoint_THTPad_D1.0mm_Drill0.5mm
TP5: +5; TestPoint_THTPad_D1.0mm_Drill0.5mm
TP6: +3.3v; TestPoint_THTPad_D1.0mm_Drill0.5mm
TP7: GND; TestPoint_THTPad_D1.0mm_Drill0.5mm
TP8: Input-PWR; TestPoint_THTPad_D1.0mm_Drill0.5mm
TP9: HV Enable; TestPoint_THTPad_D1.0mm_Drill0.5mm
U3: MAX3226; SSOP-16_5.3x6.2mm_P0.65mm; MPN MAX3226CAE+; Digi-Key MAX3226CAE+-ND
U4: CAT24C256; TSSOP-8_4.4x3mm_P0.65mm; MPN CAT24C256YI-GT3; Digi-Key CAT24C256YI-GT3OSCT-ND - Cut Tape (CT)
U5, U6: 74HC595; SSOP-16_4.4x5.2mm_P0.65mm; MPN SN74HC595ADB; Digi-Key 2156-SN74HC595ADB-ND

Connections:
+3V3: A1.17 (3V3), C10.2, C11.2, C12.2, C13.2, C16.1, J2.1, J9.1, J11.1, J12.1, J13.1, J15.1, R4.1, R6.1, R8.1, R13.1, R19.1, R20.1, R21.1, R22.1, R23.1, R25.1, R26.1, R27.1, R28.1, R29.1, TP6.1, U3.15 (VCC), U4.8 (VCC), U5.16 (VCC), U6.16 (VCC)
+5V: A1.30 (VIN), C5.2, C6.2, C7.2, C8.1, C9.1, D2.1 (K), D4.1 (K), F6.2, JP8.1 (A), JP9.1 (A), R24.2, TP5.1
/A0: A1.19 (A0), Q9.1 (G), R16.1
/A1: A1.20 (A1), J2.2, R20.2
/A2: A1.21 (A2), J9.2, R21.2
/A3: A1.22 (A3), J12.2, R22.2
/A6: A1.25 (A6), J13.2, Q11.1 (G), R18.1, R23.2
/A7: A1.26 (A7), Q10.1 (G), R17.1
/CAL: J4.2, Q7.3 (D)
/GoW: J3.4, Q8.3 (D)
/HV-PWR: D6.1 (K), F7.2, JP9.3 (B), TP4.1
/HVACa: J3.1, J4.3
/HVACb: J3.2, J4.4
/M1: J3.6, Q6.3 (D)
/M2: J3.8, Q3.3 (D)
/M3: J3.10, Q10.3 (D)
/M4: J3.9, Q11.3 (D)
/MISO: A1.15 (MISO), J15.3, R27.2
/MOSI: A1.14 (MOSI), J15.2, R25.2
/Mid_LED: J3.7, Q4.3 (D)
/Motors: C14.2, C15.2, C17.1, C18.1, C19.1, C20.1, F2.1, F3.1, F4.1, F5.1, JP9.2 (C), JP10.1 (A), Q1.10 (COM), Q2.10 (COM)
/RX1: A1.2 (RX1), JP2.2 (C), JP7.1 (A)
/SCK: A1.16 (SCK), J15.4, R29.2
/SCL: A1.24 (SCL/A5), J11.2, R26.2, U4.6 (SCL)
/SDA: A1.23 (SDA/A4), J11.3, R28.2, U4.5 (SDA)
/TX1: A1.1 (TX1), JP1.2 (C), JP5.1 (A)
/UV_Boost: J3.5, Q5.3 (D)
GND: A1.4 (GND), A1.29 (GND), C3.2, C4.1, C5.1, C6.1, C7.1, C8.2, C9.2, C10.1, C11.1, C12.1, C13.1, C14.1, C15.1, C16.2, C17.2, C18.2, C19.2, C20.2, J2.3, J9.3, J10.2, J11.4, J12.3, J13.3, J15.5, J17.3, J18.3, J19.5, PS1.3 (Gnd), PS2.3 (Gnd), Q1.9 (GND), Q2.9 (GND), Q3.2 (S), Q4.2 (S), Q5.2 (S), Q6.2 (S), Q7.2 (S), Q8.2 (S), Q9.2 (S), Q10.2 (S), Q11.2 (S), R1.2, R2.2, R3.2, R10.2, R11.2, R12.2, R16.2, R17.2, R18.2, TP7.1, U3.14 (GND), U4.4 (GND), U5.8 (GND), U5.13 (~OE), U6.8 (GND), U6.13 (~OE)
unnamed: A1.5 (D2), Q3.1 (G), R1.1
unnamed: A1.6 (D3), Q4.1 (G), R2.1
unnamed: A1.7 (D4), Q5.1 (G), R3.1
unnamed: A1.8 (D5), Q8.1 (G), R12.1
unnamed: A1.9 (D6), Q6.1 (G), R10.1
unnamed: A1.10 (D7), Q7.1 (G), R11.1
unnamed: A1.11 (D8), U5.14 (SER)
unnamed: A1.12 (D9), U5.11 (SRCLK), U6.11 (SRCLK)
unnamed: A1.13 (D10), U5.12 (RCLK), U6.12 (RCLK)
unnamed: A1.18 (AREF), TP2.1
unnamed: A1.3 (~RESET), A1.28 (~RESET), TP1.1
unnamed: C1.1, U3.2 (C1+)
unnamed: C1.2, U3.4 (C1-)
unnamed: C2.1, U3.5 (C2+)
unnamed: C2.2, U3.6 (C2-)
unnamed: C3.1, U3.3 (V+)
unnamed: C4.2, U3.7 (V-)
unnamed: D1.2 (A), F1.1
unnamed: D2.2 (A), PS1.4 (+Vout)
unnamed: D3.1 (K), JP5.2 (B)
unnamed: D3.2 (A), J17.2, J18.2, JP7.2 (B), R13.2
unnamed: D4.2 (A), J19.4
unnamed: D5.2 (A), J19.1
unnamed: D6.2 (A), PS2.4 (+Vout)
unnamed: F1.2, J10.1
unnamed: F2.2, J5.5
unnamed: F3.2, J6.5
unnamed: F4.2, J7.5
unnamed: F5.2, J8.5
unnamed: F6.1, J3.3
unnamed: F7.1, J4.1
unnamed: J1.1, R24.1
unnamed: J1.2, Q9.3 (D)
unnamed: J5.1, Q1.14 (OUT5)
unnamed: J5.2, Q1.13 (OUT6)
unnamed: J5.3, Q1.12 (OUT7)
unnamed: J5.4, Q1.11 (OUT8)
unnamed: J6.1, Q1.18 (OUT1)
unnamed: J6.2, Q1.17 (OUT2)
unnamed: J6.3, Q1.16 (OUT3)
unnamed: J6.4, Q1.15 (OUT4)
unnamed: J7.1, Q2.14 (OUT5)
unnamed: J7.2, Q2.13 (OUT6)
unnamed: J7.3, Q2.12 (OUT7)
unnamed: J7.4, Q2.11 (OUT8)
unnamed: J8.1, Q2.18 (OUT1)
unnamed: J8.2, Q2.17 (OUT2)
unnamed: J8.3, Q2.16 (OUT3)
unnamed: J8.4, Q2.15 (OUT4)
unnamed: J17.1, J18.1, JP8.2 (C)
unnamed: J19.2, JP4.2 (C)
unnamed: J19.3, JP3.2 (C)
unnamed: JP1.1 (A), JP4.1 (A)
unnamed: JP1.3 (B), U3.11 (T1IN)
unnamed: JP2.1 (A), JP3.1 (A)
unnamed: JP2.3 (B), U3.9 (R1OUT)
unnamed: JP3.3 (B), U3.8 (R1IN)
unnamed: JP4.3 (B), U3.13 (T1OUT)
unnamed: PS1.1 (En), R14.1, TP3.1
unnamed: PS2.1 (En), R15.1, TP9.1
unnamed: Q1.1 (IN1), U5.7 (QH)
unnamed: Q1.2 (IN2), U5.6 (QG)
unnamed: Q1.3 (IN3), U5.5 (QF)
unnamed: Q1.4 (IN4), U5.4 (QE)
unnamed: Q1.5 (IN5), U5.3 (QD)
unnamed: Q1.6 (IN6), U5.2 (QC)
unnamed: Q1.7 (IN7), U5.1 (QB)
unnamed: Q1.8 (IN8), U5.15 (QA)
unnamed: Q2.1 (IN1), U6.7 (QH)
unnamed: Q2.2 (IN2), U6.6 (QG)
unnamed: Q2.3 (IN3), U6.5 (QF)
unnamed: Q2.4 (IN4), U6.4 (QE)
unnamed: Q2.5 (IN5), U6.3 (QD)
unnamed: Q2.6 (IN6), U6.2 (QC)
unnamed: Q2.7 (IN7), U6.1 (QB)
unnamed: Q2.8 (IN8), U6.15 (QA)
unnamed: R4.2, U4.3 (A2)
unnamed: R6.2, U4.2 (A1)
unnamed: R8.2, U4.1 (A0)
unnamed: R19.2, U5.10 (~SRCLR), U6.10 (~SRCLR)
unnamed: U5.9 (QH'), U6.14 (SER)
Vdrive: D1.1 (K), D5.1 (K), JP8.3 (B), JP10.2 (B), PS1.2 (+Vin), PS2.2 (+Vin), R14.2, R15.2, TP8.1

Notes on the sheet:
Pwr_In
Motors
I2C
Kzin
3.3 com and power

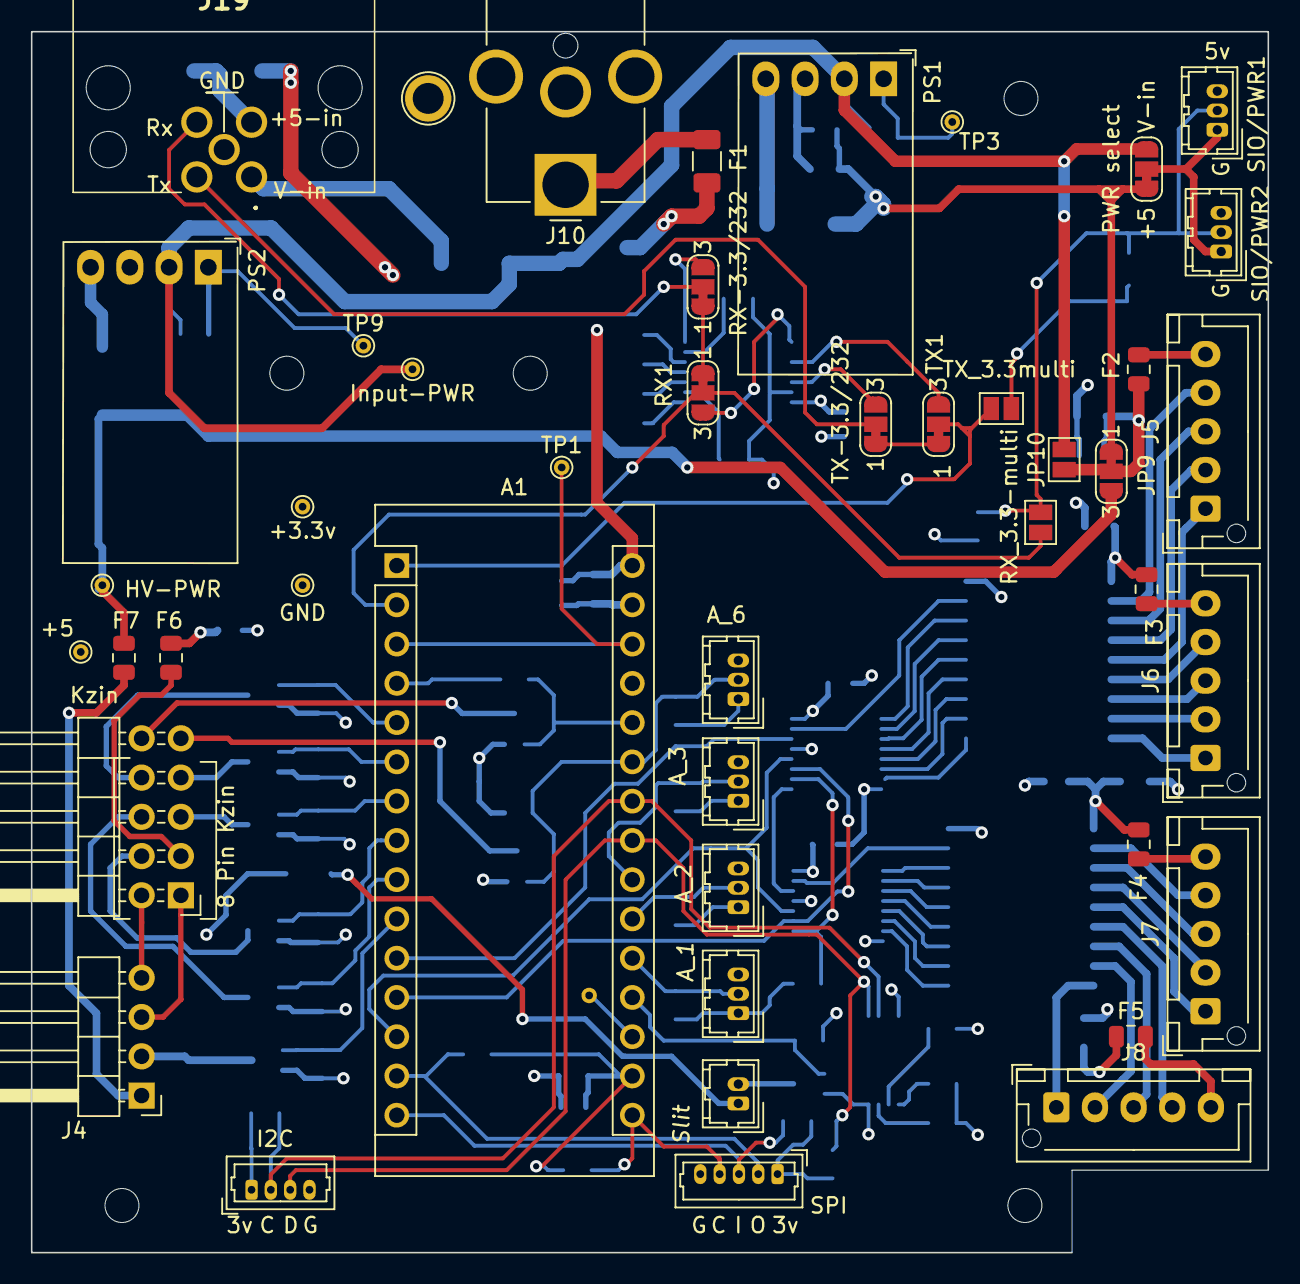
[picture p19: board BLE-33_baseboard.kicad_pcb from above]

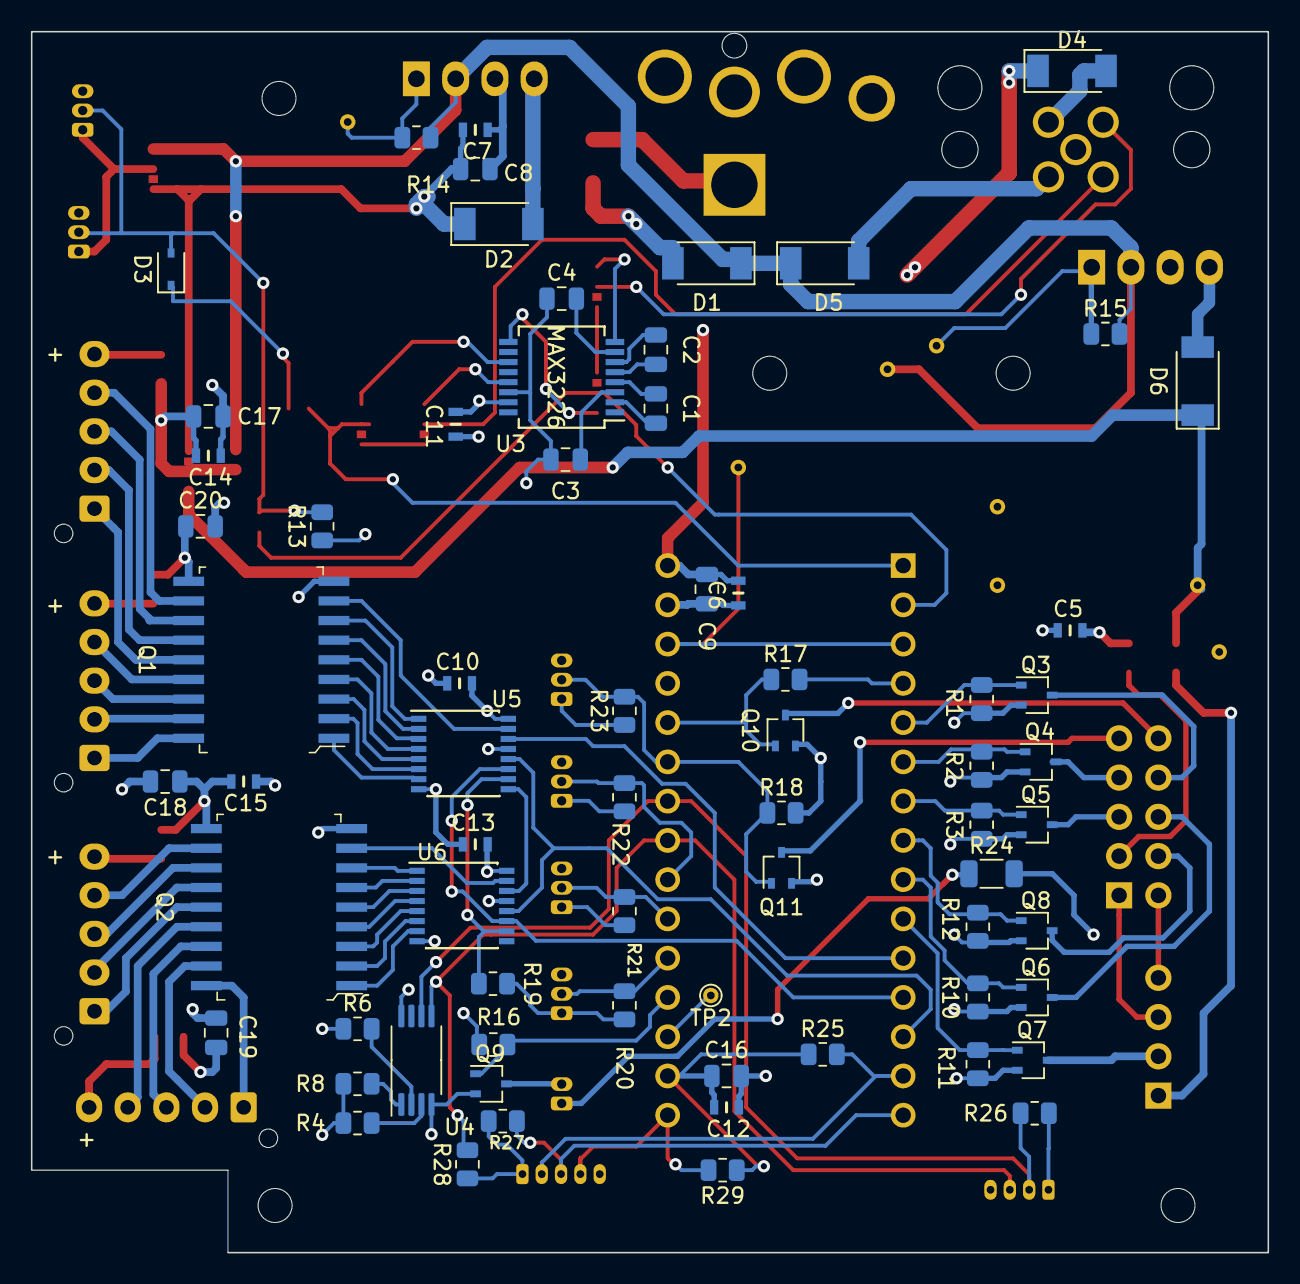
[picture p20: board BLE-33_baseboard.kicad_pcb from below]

Board: 4 copper layers, 80.0 x 79.0 mm, 112 parts (68 on the bottom side), 110 nets.

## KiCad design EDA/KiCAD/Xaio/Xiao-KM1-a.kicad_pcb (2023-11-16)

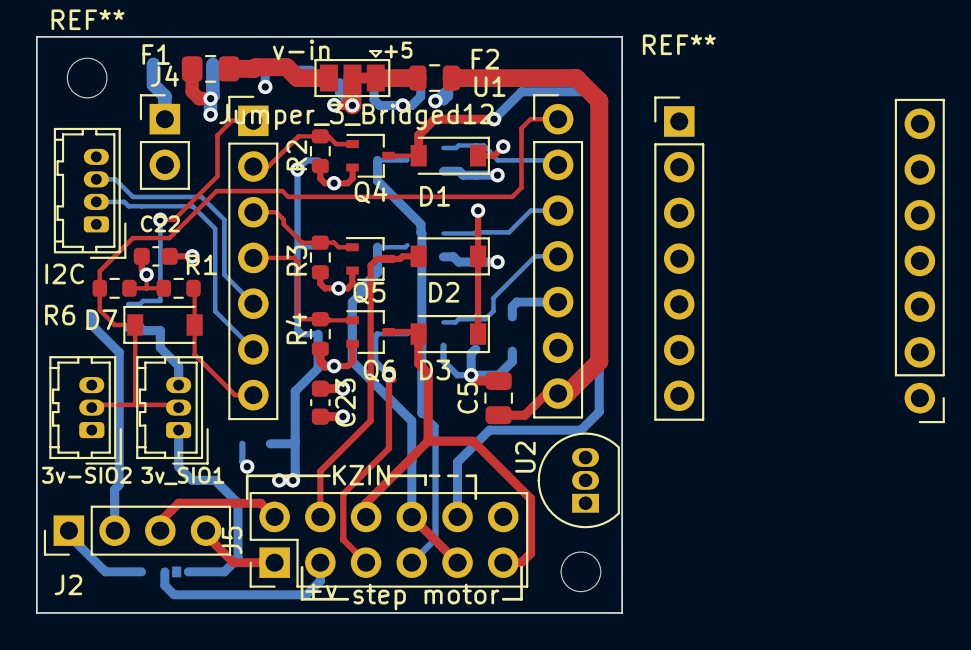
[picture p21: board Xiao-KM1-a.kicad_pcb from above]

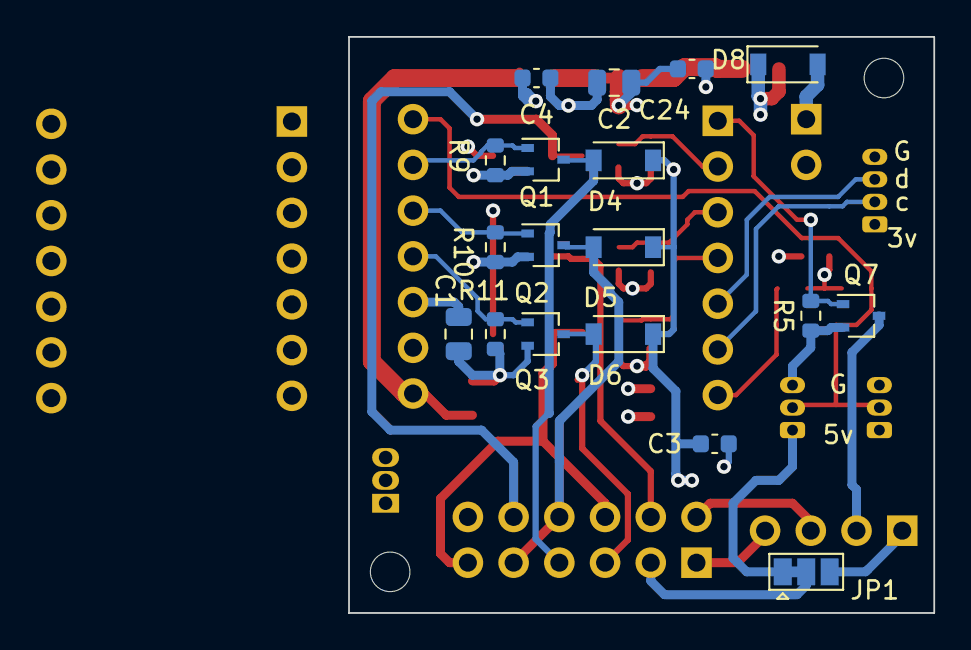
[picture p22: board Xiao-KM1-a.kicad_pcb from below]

Board: 4 copper layers, 32.5 x 32.0 mm, 44 parts (18 on the bottom side), 29 nets.

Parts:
C1, C2, C5: TAJR104M035RNJ; C_0805_2012Metric
C3, C4, C22, C23, C24: .01; C_0603_1608Metric
D1, D2, D3, D4, D5, D6, D8: MBR0580; D_SOD-123
D7: 1N4148W; D_SOD-123
F1: 500ma; Fuse_0805_2012Metric_Pad1.15x1.40mm_HandSolder
F2: Polyfuse- 350 ma; Fuse_0805_2012Metric
J1: I2C; Hirose_DF13-04P-1.25DSA_1x04_P1.25mm_Vertical
J2: Cal_PS; PinHeader_1x04_P2.54mm_Vertical
J3: 3v_SIO1; Hirose_DF13-03P-1.25DSA_1x03_P1.25mm_Vertical
J4: 277-6156-ND; PinHeader_1x02_P2.54mm_Vertical
J5: Conn_02x06_Odd_Even; PinHeader_2x06_P2.54mm_Vertical
J6: 3v-SIO2; Hirose_DF13-03P-1.25DSA_1x03_P1.25mm_Vertical
JP1, JP2: Jumper_3_Bridged12; SolderJumper-3_P1.3mm_Bridged12_Pad1.0x1.5mm
Q1, Q2, Q3, Q4, Q5, Q6, Q7: DMN3067; SOT-323_SC-70
R1, R2, R3, R4, R5, R6, R9, R10, R11: 10,000; R_0603_1608Metric
U1: SeeeduinoXIAO-on-header; Xiao-on-socket
U2: MCP1700-5002E_TO92; TO-92_Inline

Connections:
+3V3: C1.1, C22.1, C23.1, J1.1, R1.2, R6.1, U1.12
+5V: C4.1, C5.1, F2.2, J3.1, J6.1, JP1.1, U1.14, U2.3
/Broad_LED: D4.2, J5.7, Q1.3
/Cal_HV1: J2.4, J5.1
/Cal_HV2: J2.3, J5.2
/Cal_Lamp: J2.2, Q7.3
/GPIO_0: Q7.1, R5.1, U1.1
/GPIO_1: Q4.1, R2.1, U1.2
/GPIO_2: Q5.1, R3.1, U1.3
/GPIO_3: Q6.1, R4.1, U1.4
/GPIO_4: J1.3, U1.5
/GPIO_5: J1.2, U1.6
/GPIO_8: Q1.1, R9.1, U1.9
/GPIO_9: Q2.1, R10.1, U1.10
/GPIO_10: Q3.1, R11.1, U1.11
/Grain_of_Wheat: D2.2, J5.4, Q5.3
/MOTOR_POWER-IN: D8.1, F1.2
/Marker-1: D3.2, J5.6, J5.11, Q6.3
/Marker-2: D5.2, J5.8, J5.9, Q2.3
/Marker-3: D1.2, J5.10, Q4.3
/UART_RX: D7.1, J3.2, J6.2, R6.2, U1.8
/UART_TX: D7.2, R1.1, U1.7
/UV-Boost: D6.2, J5.5, Q3.3
GND: C1.2, C2.2, C3.2, C4.2, C5.2, C22.2, C23.2, C24.2, J1.4, J3.3, J4.2, J6.3, Q1.2, Q2.2, Q3.2, Q4.2, Q5.2, Q6.2, Q7.2, R2.2, R3.2, R4.2, R5.2, R9.2, R10.2, R11.2, U1.13, U2.1
Motor_PWR: C2.1, C3.1, C24.1, D1.1, D2.1, D3.1, D4.1, D5.1, D6.1, J2.1, JP1.3, JP2.2, U2.2
unnamed: D8.2, J4.1
unnamed: F1.1, JP2.3
unnamed: F2.1, JP2.1
unnamed: J5.3, JP1.2

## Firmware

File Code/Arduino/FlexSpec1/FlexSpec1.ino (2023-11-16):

String CodeVersion = "4.1.2";
String CodeDate = "9/27/2023";
String CodeLocation = "SAS_NA1_3D_Spectrograph/V2-FS1Code/demos/My-FS1_Arduino_control_code_V4.1.2";

//                    This code is for Gregs board V4
//    This added the "A" routine to display all of the functions on request.

//&&&&&&&&&&&&&&&&&&&&&&&&&&&&&&&&&&&&&&&&&&&&&&&&&&&&&&&&&&&&&&&&&&&&&&&&&&&&&&&&&&&
// IF RUNING WITH USB MAKE SURE THAT THE SERIAL MONITOR HAS "NO LINE ENDING" SELECTED
//&&&&&&&&&&&&&&&&&&&&&&&&&&&&&&&&&&&&&&&&&&&&&&&&&&&&&&&&&&&&&&&&&&&&&&&&&&&&&&&&&&&

/*This Sketch takes my_serial inputs as controls for moving 28BYJ-48 stepper motors
   controlling collimating lens and grating position, Calibration and Flat lamps
   and location LEDs.

   Inputs are: integers and specific command letters entered through the my_serial Read
   function, the command notation being: NNNN <CR> for CCW rotation or -NNNN<CR> for
   CW rotation.
   Alpha inputs are:

  A<CR> Routine to display all functions
  B<CR> lights the Blue
  C<CR> Configuration to set the grating lines per mm
  F<CR> MOVES collimating lens focus
  G<CR> lights the Green
  H<CR> Home The Grating
  I<CR> lights the incandescent Grain of Wheat Flat lamps, PWM 0 - 100%.
  J<CR> Used to center zero order to focus on slit
  L<CR> lights the LED Flat lamps, PWM 0 - 100%.
  M<CR> Reset collimating Focuses to zero
  N<CR> lights the Neon bulb(s)
  O<CR> Turns all lamps off
  Q<CR> Query status of the spectrometer
  R<CR> Controls The Red LED With PWM 0 - 100%
  S<CR> This Opens And Closes The Shutter
  U<CR> Lights the UV Boost, PWM 0 - 100%.
  V<CR> View the slit with backlight
  W<CR> rotate the grating to center desired wavelength

  Z<CR> This sets the collimating lens position = 0 (home)
         (This should only be done once on initialization of physical focus)

  ?<CR> Defines the grating and collimating motor direction
        (This should only be done once on initialization or if a motor is changed
        depending on the manufacture some motors run in oposit direction)

   ALL COMMANDS WORK HIGH AND LOWER CASE

   All movement is ended with the motor rotating in the CW direction'
   and coils de-energized.

   Author: Clarke Yeager
   Version 4.1.2
   27 October 2023
*/

#include <Servo.h>  // loads the Servo.h library
#include "Wire.h"
#include "I2C_eeprom.h"

I2C_eeprom ee(0x57, I2C_DEVICESIZE_24LC256);  //establishes the I2C address for the 24LC256 EEPROM


//                               SPECTROGRAPH PROFILE
//              &&&& These are parameters that may need to be adjusted! &&&&
//  ===============================================================================================
#define my_serial Serial    // Serial1 is used with Putty, change this to Serial to use USB
int minimum = 3500;         // minimum selectable wavelength to be centered
int maximum = 7800;         // maximum selectable wavelength to be centered
int zeroOrderOffset;        // This is an offset number needed to center the slit after homing
int BkLashCount = 120;      // This is how many steps backlash goes
int minSteps = -700;        // The minimum negative steps are allowed in jog mode
int maxSteps = 450;         // The maximum positive steps are allowed in jog mode
float scaleFactor = .0540;  //gain to calibrate wavelength per motor step
float enterTime = 1500;     // This determines how long you have to enter a value after start of entry
int shutterOpen = 10;       //This is the value that determines the position of the open shutter
int shutterClosed = 140;    //This is the value that determines the position of the closed shutter
//  ---------------------------------------------------------------------------------------------------

//                      &&&& EEPROM address allocation &&&&
//  ===============================================================================================
int zeroOrderOffsetAddress = 12;  // Each address uses two bytes
int focusAddress = 14;            // focus location store two bytes
int focusPositionAddress = 16;    // focus location store two bytes
int negativeAddress = 18;         // focus location store two bytes
int inputAddress = 20;            // focus input offset;
int motorAddress = 22;            // Motor direction value
int gratingDirAddress = 24;       // grating motor direction value
int focusDirAddress = 26;         // focus motor direction value
int motorInitFlagAddress = 28;    // Motor initialization Flag
int posAddress = 30;              // Shutter position vlaue
int configurationAddress = 32;    // This is FS1 configuration

//  ---------------------------------------------------------------------------------------------------

int calLamp = 7;           // calibration lamp neon or Relco
int incandescentLamp = 4;  // this is the pin assignment for the Grain of wheat lamps
int UVBoostLED = 5;        // this boost the UV
int blueLED = 2;           // this is a blue marker
int greenLED = 9;          // this is a green marker
int slitLED = 10;          // this is the pin to backlight the slit
int flatLED = 3;           // this is a broad flat light
int redLED = 6;            // this is a red marker
int shutterPin = A1;       // this pin drives the shutter
int dly = 2;               //used to set the delay to control motor speed
int steps = 0;             //used to keep track of how many steps the stepper motor takes
int term = 8;              //this will be set to 0 when the desired number of motor sequence has been reached
int gsteps = 0;            // used to count the number of grating motor steps
int Position = 0;          // used to keep track of the grating position
int gratPosition = 0;      // used to keep track of the grating position
int gratStatus = 0;        // keeps track of the grating status
int colSteps = 997;        // collimating step count
int gratSteps = 997;       // grating step count
int zeroOrderSteps = 0;    // Zero order step count to center the slit in zero order
int zOrderSteps = 0;
int RequestedSteps = 0;  // The number of steps requested in jog mode
int zeroPosition = 0;    // used to keep track of the grating position
int PhaseHist;           // this is used to keep track of the last motor phase that was used
int orderPhaseHist;
int stepperPhase;
int zeroOrderPhase;
int zPhase = 0;
int phase;
int data = 20;
char savedFlag;      // Flag to show the homing has been done
int homed = 0;       // set to 1 when the grating has been homed
int colStepHist;     // keeps track of the collimating history if needed
int colPhaseHist;    // keeps track of the collimating motor history if needed
int gratStepHist;    // keeps track of the grating history if needed
int gratPhaseHist;   // keeps track of the grating motor history if needed
int magnetNew = 0;   //used to sense what magnetic polarity the Hall polarity sees for homing
int magnetOld = 0;   //remember the previous state so a transition can be recognized for homing
int magnetPin = A2;  //used for the homing Hall sensor
int CW = 0;          //keeps track if the rotation is CW or CCW
float wavelength;    //wavelength in Angstroms
int cal = -1;        // Relco calibration lamp starts off, LED will toggle between on and off
int UVBoost = -1;    // UV Boost LED starts off, LED will toggle between on and off
int incandescent;    // incandescent grain of wheat lamps start off
float GowPWM = 0;    // grain of wheat duty cycle (0 - 255)
float GowPWMnew;     // entered grain of wheat duty cycle
int blue = -1;       // Blue marker start off, LED will toggle between on and off (4700 angstroms)
int green = -1;      // green marker start off, LED will toggle between on and off, (5000 angstroms)
int slit = -1;       // slit illuminator to backlight the slit
int flat;            // Flat LED start off
float flatPWM = 0;   // Flat LED duty cycle (0-255)
float flatPWMnew;    // Entered flat LED duty cycle
int red;             // Red LED start off, (6590 angstroms)
float redPWM = 0;    // Red LED duty cycle (0-255)
float redPWMnew;     // Entered Red LED duty cycle
float UVPWM = 0;  // UV LED duty cycle (0-255)
float UVPWMnew;   // Entered UV LED duty cycle

int shutterStatus = 1;  // shutter starts open, it will toggle from open to closed
int servoPin = A1;      // Pin used for the shutter
int servoPos;           // Keeps track if the shutter is open or closed

int pos;               // The current position of the shutter servo
int posHist;           // Keeps track of where the shutter servo has been
int servo_delay = 25;  // Settle time for shutter moves
Servo shutterServo;    // Connect to the servo
int output;

int motorFlag;
int motorDir;
int gratingDir;
int focusDir;
int stepHist;

int colLocation;
float colPos;
float inputSteps;
int lastPosition;
int negativeFlag;
int negFlagHist;
int focusDirCode;
int focus;
int focusPosition;
int gratingDirCode;
int input;
int tempNegativeFlag;
int grating_mm;
int POR = 0;
int test;

float result;

// This void deals with the 2's compliment for negative numbers and large numbers < 32,768
//  ===============================================================================================

void write2BytesIntIntoEEPROM(int focusAddress, int number) {
  ee.writeByte(focusAddress, (number >> 8) & 0xFF);  //This writes two bytes to EEPROM, byte1 and byte2
  ee.writeByte(focusAddress + 1, number & 0xFF);     // byte1 is shifted and then byte2 is added to the result of the shift
}

int read2BytesFromEEPROM(int focusAddress)  //This reads two bytes to EEPROM, byte1 and byte2
{
  return (ee.readByte(focusAddress) << 8) + ee.readByte(focusAddress + 1);
}


// Patterns for collimator motor drive, 8 drive patterns,
//  ===============================================================================================
int dataArray1[8] = { 0b00000001, 0b00000011, 0b00000010, 0b00000110, 0b00000100, 0b00001100, 0b00001000, 0b00001001 };  //motor 1 CW
int dataArray2[8] = { 0b00001001, 0b00001000, 0b00001100, 0b00000100, 0b00000110, 0b00000010, 0b00000011, 0b00000001 };  //motor 1 CCW

// Patterns for grating motor drive, 8 drive patterns,
//  ===============================================================================================
int dataArray4[8] = { 0b00010000, 0b00110000, 0b00100000, 0b01100000, 0b01000000, 0b11000000, 0b10000000, 0b10010000 };  //motor 2 grating CW
int dataArray3[8] = { 0b10010000, 0b10000000, 0b11000000, 0b01000000, 0b01100000, 0b00100000, 0b00110000, 0b00010000 };  //motor 2 grating CCW

void displayFunctionList();
void functionList();
void enterFunction();
void resetFocus();
void homing();
void backlash();

//&&&&&&&&&&&&&&&&&&&&&&&&&&&&&&&&&&&&&&&&&&&&&&
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

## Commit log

2021-06-29 Updated the info on using arduinos
2021-07-16 Created a Kzin class specifically for that device, with sliders for intensity 0..100%. Modified FlexSpec.py to use the new KzinBokey module
2021-08-27 Changed the message across the board to be right and consistent. Handled the home with a simple state variable. Updated the server, tested a bit more this time.
2021-09-14 Error in bash script, missing ;; for a case.
2022-04-21 Adding placeholders
    [FS1_guide_lens_calculator.xlsx]
2022-07-17 Added a driectory for Tools, for spreadsheets, and other tooly things.
    [FS1_guide_lens_calculator.xlsx]
2022-07-17 Moved to tools, removed spaces in file name.
    [FS1 guide lens calculator.xlsx]
2022-07-17 Duplicate removed
    [FS1_guide_lens_calculator.xlsx]
2022-07-22 Added EEPROM basic code for handling the contents of the main json string back from the eeprom device.
2022-08-09 Unification of the code, adjusting variables to reflect what they actually do. Display.py is replaced with the virtually identical FlexPublish.py to have the filename reflect what it does, and to sta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
    Error handling was beefed up a bit, some dead code removed.
    Comments were fixed from a fast cut/paste approach early on
    to have the comments actually mean something for thier code.
    Some pythonic typing was added. Dunder's added in some places,
    more to do.
    The tabs were renamed in FlexSpec.py to reflect the actual
    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
2022-09-14 Added the changes to RunFlexSpec to properly attach to a remotge machine
2022-10-21 added FlexCRC -- the counterpart of Arduino code.
2022-11-02 Incremental checkin
    The network was updated to be url based.
    The main flexspec has an Flex_Instrument instance, allows name change
    to be propagated.
    Added a few placeholder values -- need more
    Started removing the device name, need to put that back.
    This is a placeholder for the current work.
2023-01-21 Script to find arduino TTY port
2023-01-27 Script to find arduino tty port names
2023-11-16 The source code for the main FlexSpec1 Board.
2023-11-16 Added BLE Baseboard V2 to the repo.
    [BLE-33_baseboard-B_Cu.gbr, BLE-33_baseboard-B_Mask.gbr, BLE-33_baseboard-B_Paste.gbr, BLE-33_baseboard-B_SilkS.gbr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]
2023-11-16 Added Xaio Standalone Board files.
    [Xiao-B1.kicad_pcb, Xiao-B1.sch, Xiao-KM1-a.kicad_pcb]
